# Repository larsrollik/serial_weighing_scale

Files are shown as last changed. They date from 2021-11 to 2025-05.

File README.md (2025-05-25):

# Serial Weighing Scale
Arduino-based cheap precision weighing scale for readout via serial communication.

***
Version: "2.0.4"

Precision weighing scales that include serial port communication usually come at considerable cost. This project showcases an affordable alternative.
Using readily available electronics parts, the scale's measurements can be read via serial communication by a simple Python class.

_Note:_ The design could easily be extended with an Arduino display to show the measurements.

### Bill of Materials
- Arduino Uno (including USB-A to USB-B cable)
- Load cell amplifier HX711 (Sparkfun), e.g. from mouser.co.uk: 474-SEN-13879
- Load cell (100g and 500g cells used), e.g. from mouser.co.uk: 474-SEN-14727 or 474-SEN-14728
- Jumper wires, pin headers, nylon spacers for electronics
- Acrylic or other material of choice for case and load cell mount
- HX711 arduino library from [olkal/HX711_ADC](https://github.com/olkal/HX711_ADC)

### Build
1. Load .ino onto Arduino (via Arduino IDE or commandline like `arduino --board arduino:avr:uno --port /dev/ttyACM0 --upload serial_scale.ino`)
2. Assemble electronics, e.g. as described in this [HX711 wiring tutorial]
3. Print 3D components from [drawings](./drawings_for_3D_printing) (Drawings named `model` are only for design, no need to print these)
4. Move electronics into case
5. Calibrate scale via Arduino IDE serial monitor commands. See below for communication protocol for calibration.

### Usage
1. Connect scale via USB to machine that is going to read the measurements from the scale
2. Interact via python `SerialScale` object:

##### Open connection with `SerialWeighingScale` object & perform standard operations on it
```python
import numpy as np
import time

from serial_weighing_scale import SerialWeighingScale

serial_port = "/dev/ttyACM0"  # for Unix systems. "COM1" on Windows systems
scale = SerialWeighingScale(serial_port=serial_port)
scale.connect()

while not scale.is_ready:
    time.sleep(.1)

# Perform standard operations
scale.tare()  # Tare scale
scale.read_weight()  # Take single measurement
scale.read_weight_repeated(n_readings=5, inter_read_delay=.1)  # Get n readings
scale.read_weight_reliable(n_readings=5, inter_read_delay=.1, measure=np.mean)  # Get statistic of n readings

```

##### Open connection by testing specific serial ports sequentially
```python
from serial_weighing_scale import connect_serial_scale

scale = connect_serial_scale(serial_port_list=["/dev/ttyACM0", "/dev/ttyACM1"])

# ...

```

### Communication protocol for messages between python and Arduino

- Tare scale: send "t" -> Tare scale & Arduino confirms with "t"
- Read scale: send "w" -> Arduino returns latest reading
- Read calibration factor: send "f" -> Arduino returns calibration factor

- Calibrate scale: send "c" + weight of known mass
  - Arduino confirms by sending known mass value back
  - Send "a" once known mass was placed on scale -> Arduino performs calibration & returns new calibration factor that needs to be added to `serial_scale.ino`

### TODO
- [ ] Add calibration routine to .ino & .py
- [ ] Add test curve to .py

## NOTES
- calibration for first scale with 28.22g weight: -3150
- calibration for second scale with 28.22g weight: -2894

### Contributors
Code & electronics by Lars Rollik.
Scale 3D printing drawings by Simon Townsend ([Advanced Manufacturing FabLabs], Sainsbury Wellcome Centre).
Thanks to Benjamin Hahl for useful input on the design.

[Advanced Manufacturing FabLabs]: https://www.sainsburywellcome.org/web/content/fablab
[HX711 wiring tutorial]: https://learn.sparkfun.com/tutorials/load-cell-amplifier-hx711-breakout-hookup-guide

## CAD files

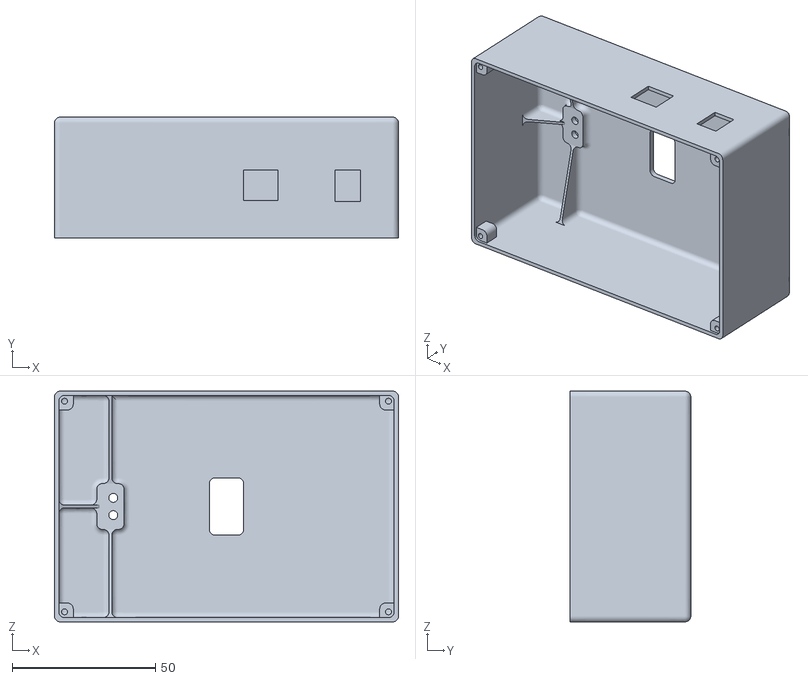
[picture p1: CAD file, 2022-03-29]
drawings_for_3D_printing/serial_weighing_scale__case_main.stl
120.0 x 42.1 x 80.5

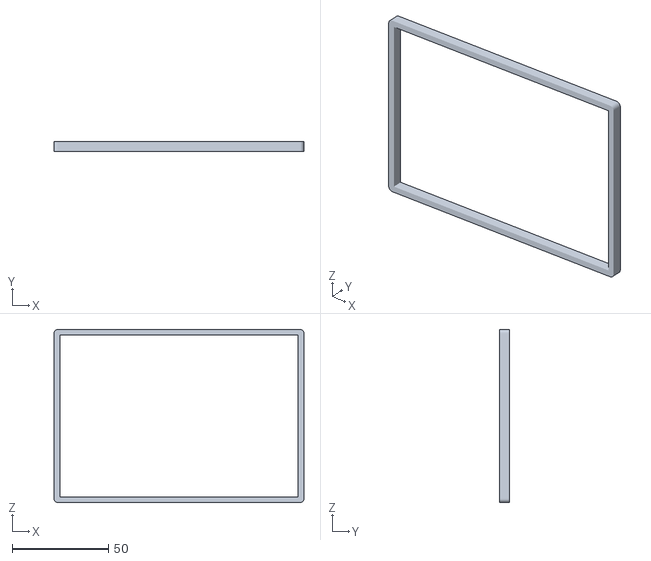
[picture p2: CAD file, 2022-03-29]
drawings_for_3D_printing/serial_weighing_scale__platform_edge_overhang.stl
130.0 x 5.00 x 90.0

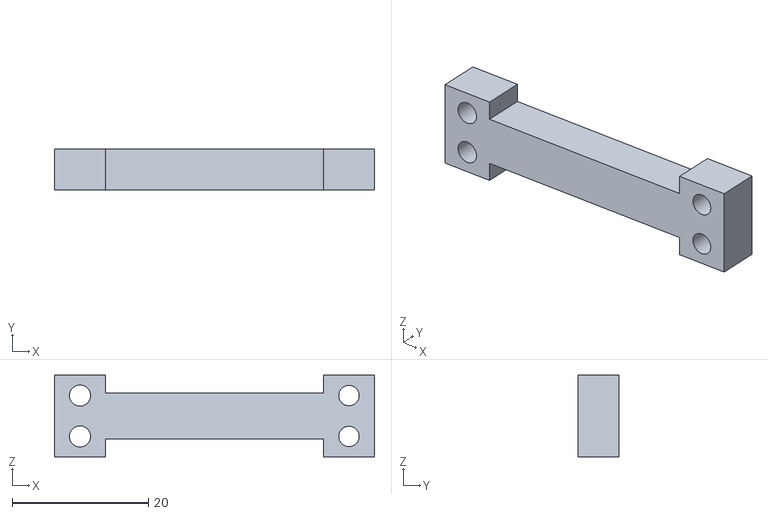
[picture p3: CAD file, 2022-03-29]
drawings_for_3D_printing/serial_weighing_scale__model_load_cell.stl
47.0 x 6.00 x 12.0

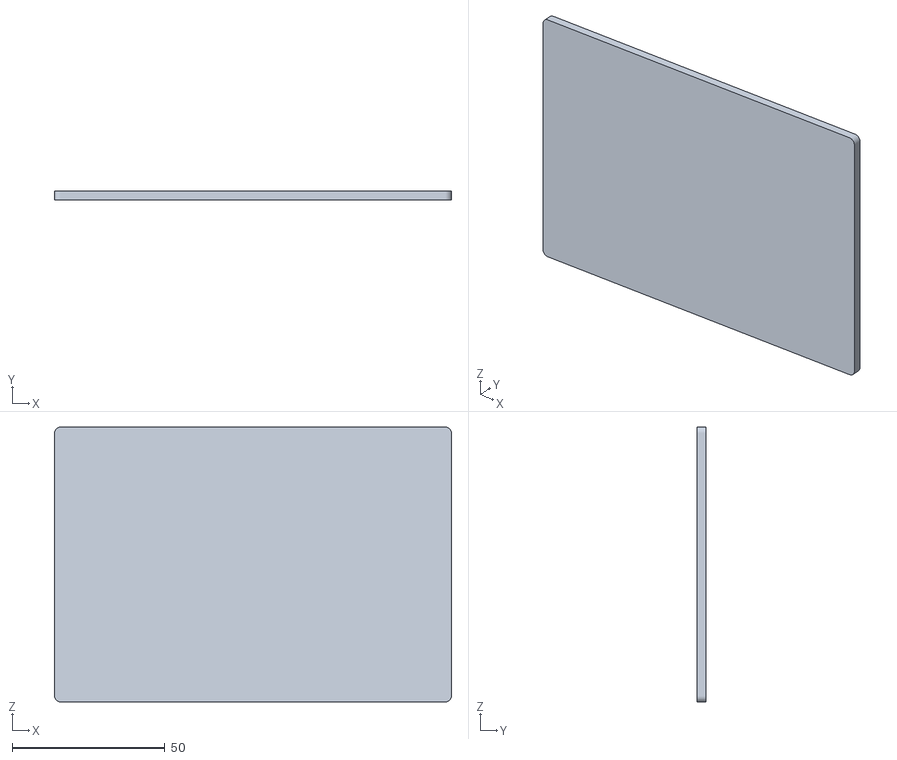
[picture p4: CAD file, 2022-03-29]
drawings_for_3D_printing/serial_weighing_scale__platform.stl
130.0 x 3.00 x 90.0

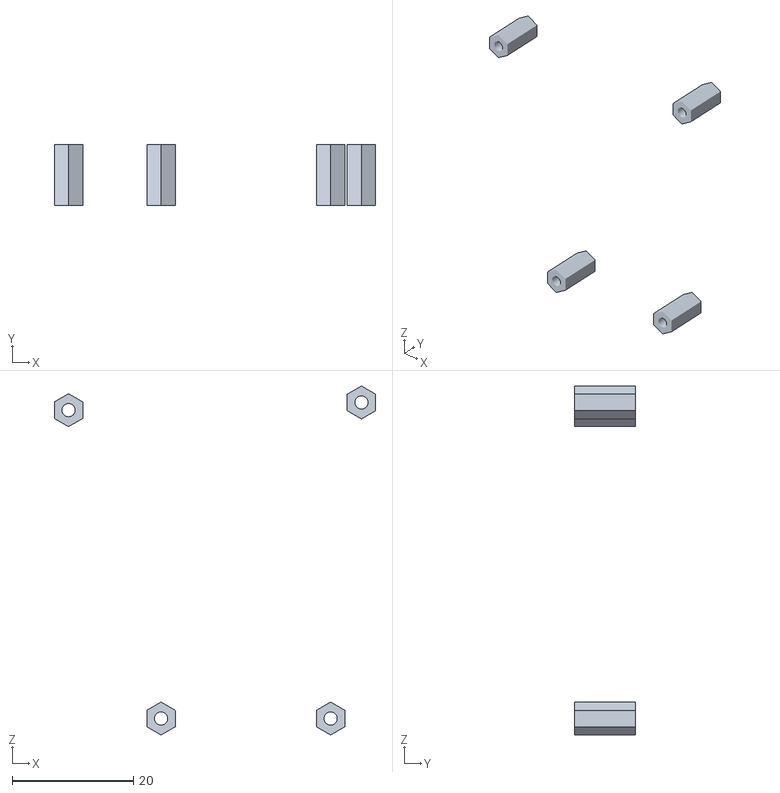
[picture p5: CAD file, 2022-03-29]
drawings_for_3D_printing/serial_weighing_scale__model_standoffs.stl
53.0 x 10.00 x 57.5

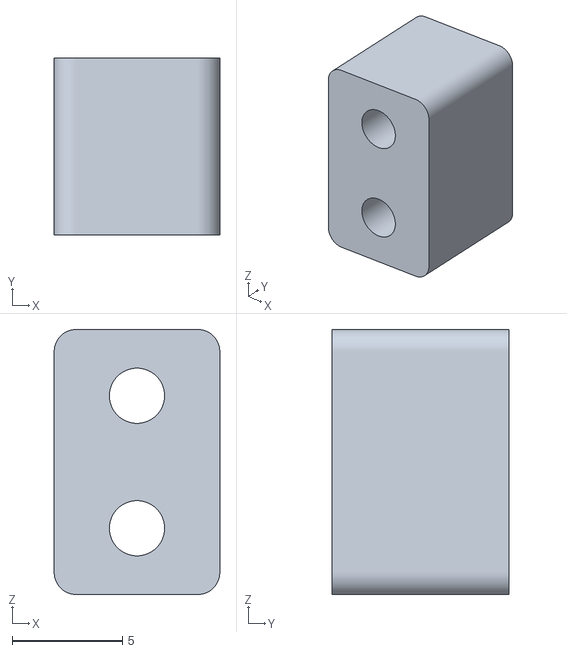
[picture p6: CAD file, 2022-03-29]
drawings_for_3D_printing/serial_weighing_scale__platform_spacer.stl
7.50 x 8.00 x 12.0

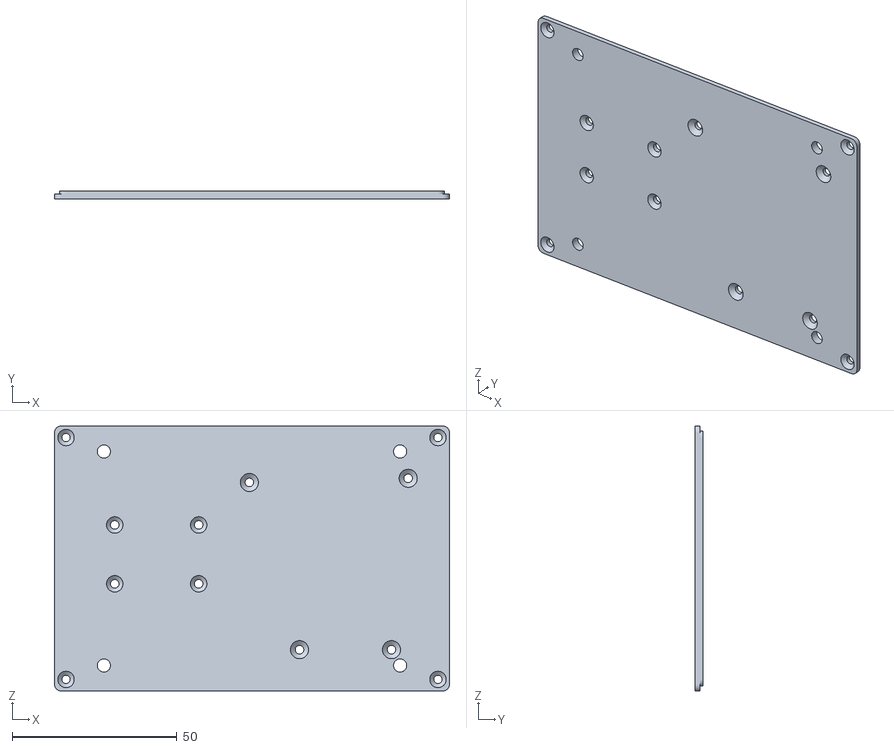
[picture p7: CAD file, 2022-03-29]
drawings_for_3D_printing/serial_weighing_scale__case_base.stl
120.0 x 2.50 x 80.5

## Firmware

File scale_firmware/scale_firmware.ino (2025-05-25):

/*
  Firmware version: "2.0.4"
  -------------------------------------------------------------------------------------
  Adapted example from HX711 library for `serial-weighing-scale`. Lars Rollik, nov2021.
  github.com/larsrollik/serial-weighing-scale
  -------------------------------------------------------------------------------------
  HX711_ADC
  Arduino library for HX711 24-Bit Analog-to-Digital Converter for Weight Scales
  Olav Kallhovd sept2017
  -------------------------------------------------------------------------------------
*/

#include <HX711_ADC.h>

// DEFINITIONS
#define CMD Serial
#define HX711_DOUT 2      // DATA
#define HX711_SCK 3       // CLOCK
#define SAMPLES_IN_USE 1  // number of samples to average for measurement, less will cause more noise but faster response
// #define CALIBRATION_FACTOR -3150  // CHANGE THIS VALUE FROM CALIBRATION RESULT  // scale 1
#define CALIBRATION_FACTOR -2630  // CHANGE THIS VALUE FROM CALIBRATION RESULT  // scale 2
#define SCALING_FACTOR 1.0
#define STABILIZING_TIME 2000  // precision right after power-up can be improved by adding a few seconds of stabilizing time
#define PERFORM_TARE true      // set to false if you don't want tare to be performed in the next step
#define DEBUG_PRINT false
#define ID_STRING "<SerialWeighingScale>"
#define BUFFER_SIZE 10

// INSTANCE of LoadCell object
HX711_ADC LoadCell(HX711_DOUT, HX711_SCK);

float buffer[BUFFER_SIZE];
uint8_t bufIndex = 0;
bool bufFilled = false;
// Sampling flag set by ISR
volatile bool sampleFlag = false;

void setup() {
  // establish communication
  CMD.begin(115200);

  // initialize the scale
  LoadCell.begin();
  LoadCell.start(STABILIZING_TIME, PERFORM_TARE);
  LoadCell.setSamplesInUse(SAMPLES_IN_USE);
  LoadCell.setGain(128);

  if (LoadCell.getTareTimeoutFlag()) {
    logMessage("Timeout, check MCU>HX711 wiring and pin designations");
    while (1)
      ;
  } else {
    LoadCell.setCalFactor(CALIBRATION_FACTOR);
  }

  while (!CMD)
    ;

  identifyMyself();

  if (DEBUG_PRINT)
    logMessage("ready");

  // Initialize buffer
  for (int i = 0; i < BUFFER_SIZE; i++) {
    buffer[i] = 0;
  }

  // --- Timer1 Setup for 100ms interrupts ---
  noInterrupts();  // Disable interrupts during setup

  TCCR1A = 0;  // Clear Timer/Counter Control Registers
  TCCR1B = 0;
  TCNT1 = 0;  // Clear timer counter

  // Set compare match register for 100ms interval
  // Formula: OCR1A = (16*10^6) / (prescaler * frequency) - 1
  // For 10Hz (100ms): OCR1A = 16,000,000 / (64 * 10) - 1 = 24,999
  OCR1A = 24999;
  TCCR1B |= (1 << WGM12);               // CTC mode
  TCCR1B |= (1 << CS11) | (1 << CS10);  // Prescaler 64
  TIMSK1 |= (1 << OCIE1A);              // Enable Timer1 compare interrupt

  interrupts();  // Enable global interrupts

}  // setup


void loop() {
  if (sampleFlag) {
    sampleFlag = false;

    if (LoadCell.update()) {
      addToBuffer(LoadCell.getData());
    }
  }//if

  //   LoadCell.refreshDataSet();
  // LoadCell.update();
  //   float i = LoadCell.getData() / SCALING_FACTOR;

  static byte startByte = '<';
  static byte stopByte = '>';
  static byte commandChar;
  // static uint16_t int1;
  // static uint16_t int2;

  static bool receiving = false;
  static byte buffer[256];
  static int bufferIndex = 0;

  // Check if data is available
  while (CMD.available()) {
    byte incomingByte = CMD.read();

    if (incomingByte == startByte) {
      // Start receiving message
      receiving = true;
      bufferIndex = 0;
      continue;
    }

    // EVAL: Stop receiving message and process data
    if (incomingByte == stopByte) {
      receiving = false;
      commandChar = buffer[0];

      switch (commandChar) {
        case 'i':
          // identify as scale
          identifyMyself();
          break;

        case 'w':
          // read weight

          if (DEBUG_PRINT)
            logMessage("reading weight");

          // readWeight();
          CMD.println(String(getRollingAverage(2)));
          break;

        case 't':
          // tare scale
          tare_scale();
          break;

        case 'c':
          // calibrate scale (factor)
          calibrate();
          break;

        case 'f':
          // read calibration factor
          CMD.println(String(CALIBRATION_FACTOR));
          break;

        default:
          if (DEBUG_PRINT)
            logMessage("Invalid command");
          break;
      }
    }  // EVAL

    // RX
    if (receiving) {
      // Store received bytes in buffer
      if (bufferIndex < sizeof(buffer)) {
        buffer[bufferIndex++] = incomingByte;
      }
    }  // RX
  }    // while
}  // loop


// Timer interrupt handler for sampling
void sampleLoadCell() {
  if (LoadCell.update()) {
    float sample = LoadCell.getData();  // Read sample from HX711
    addToBuffer(sample);
  }
}

// Timer1 ISR every 100ms
ISR(TIMER1_COMPA_vect) {
  sampleFlag = true;
}

// Add the new sample to the buffer
void addToBuffer(float val) {
  buffer[bufIndex++] = val;
  if (bufIndex >= BUFFER_SIZE) {
    bufIndex = 0;
    bufFilled = true;
  }
}

float getRollingAverage(int precision) {
  uint8_t size = bufFilled ? BUFFER_SIZE : bufIndex;
  if (size == 0) return 0.0;

  float sum = 0;
  for (uint8_t i = 0; i < size; i++) sum += buffer[i];
  float avg = sum / size;

  // Round to specified precision
  float factor = pow(10, precision);
  return round(avg * factor) / factor;
}


void identifyMyself() {
  CMD.println(ID_STRING);
}

void logMessage(const String& msg) {
  CMD.print("LOG: ");
  CMD.println(msg);
}  // end:log


void sendFloatAsBytes(float value) {
  union {
    float f;
    byte b[4];
  } data;

  data.f = value;

  for (int i = 0; i < 4; i++) {
    CMD.write(data.b[i]);
  }
}  // end:float

void readWeight() {
  if (DEBUG_PRINT)
    logMessage("fct: readWeight");

  // LoadCell.refreshDataSet();
  LoadCell.update();
  float i = LoadCell.getData() / SCALING_FACTOR;
  // sendFloatAsBytes(i);
  CMD.println(String(i));
}  // end: read weight

int tare_scale() {
  // LoadCell.tareNoDelay();  // Start tare without delay
  LoadCell.tare();  // Start tare (blocking)
}  // end: tare


void calibrate() {
  LoadCell.setCalFactor(1.0);  // Reset calibration factor to default
  tare_scale();                // Tare the scale before calibration

  logMessage("Make sure to send 'c' calibrate command and known mass float each without line ending!");
  logMessage("Please enter the known mass (in grams) and press Enter:");
  while (!CMD.available()) {
    // Wait for the user to submit the known mass
    delay(100);
  }

  // Read the known mass input from serial
  float known_mass = CMD.parseFloat();
  logMessage("Known mass received: ");
  logMessage(String(known_mass));  // Confirm receipt of known mass

  logMessage("Now, please place the known weight on the scale and press 'a' to begin calibration.");

  boolean weight_added = false;
  while (!weight_added) {
    if (CMD.available()) {
      char cmdChar = CMD.read();  // Read input from user
      LoadCell.update();          // Update load cell reading

      // Wait for user to confirm the weight is placed and press 'a'
      if (cmdChar == 'a') {
        LoadCell.refreshDataSet();  // Refresh data from the load cell
        float new_calibration_factor = LoadCell.getNewCalibration(known_mass);

        logMessage("New calibration factor: ");
        logMessage(String(new_calibration_factor));

        weight_added = true;  // Calibration is complete
      }
    }
    delay(10);  // Short delay to avoid excessive CPU usage
  }             // while
}  // end: calibrate

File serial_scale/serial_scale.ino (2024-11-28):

/*
   Adapted example from HX711 library for `serial_weighing_scale`. Lars Rollik, nov2021.
   github.com/larsrollik/serial_weighing_scale
   -------------------------------------------------------------------------------------
   HX711_ADC
   Arduino library for HX711 24-Bit Analog-to-Digital Converter for Weight Scales
   Olav Kallhovd sept2017
   -------------------------------------------------------------------------------------
*/

#include <HX711_ADC.h>

// DEFINITIONS
#define CMD Serial
#define HX711_DOUT 2              // DATA
#define HX711_SCK 3               // CLOCK
#define SAMPLES_IN_USE 1          // number of samples to average for measurement, less will cause more noise but faster response
#define CALIBRATION_FACTOR -3150  // CHANGE THIS VALUE FROM CALIBRATION RESULT
#define SCALING_FACTOR 1.0
#define STABILIZING_TIME 2000  // precision right after power-up can be improved by adding a few seconds of stabilizing time
#define PERFORM_TARE true      // set to false if you don't want tare to be performed in the next step
#define DEBUG_PRINT false


// INSTANCE of LoadCell object
HX711_ADC LoadCell(HX711_DOUT, HX711_SCK);


void setup() {
  LoadCell.begin();
  LoadCell.start(STABILIZING_TIME, PERFORM_TARE);
  LoadCell.setSamplesInUse(SAMPLES_IN_USE);

  CMD.begin(115200);
  while (!CMD)
    ;

  if (LoadCell.getTareTimeoutFlag()) {
    CMD.println("Timeout, check MCU>HX711 wiring and pin designations");
    while (1)
      ;
  } else {
    LoadCell.setCalFactor(CALIBRATION_FACTOR);

    if (DEBUG_PRINT)
      CMD.println("READY");
  }
}

void loop() {
  //   LoadCell.refreshDataSet();
  //   LoadCell.update();
  //   float i = LoadCell.getData() / SCALING_FACTOR;

  if (CMD.available()) {
    char cmdChar = CMD.read();

    if (DEBUG_PRINT) {
      CMD.println("cmd: " + String(cmdChar));  // Print cmdChar for debugging
    }

    if (cmdChar == 'w') {
      unsigned long startTime = millis();

      LoadCell.refreshDataSet();
      LoadCell.update();
      float i = LoadCell.getData() / SCALING_FACTOR;
      CMD.println(i);

      if (DEBUG_PRINT) {
        unsigned long endTime = millis();  // Record the end time
        // Calculate and print the elapsed time
        unsigned long dt = endTime - startTime;
        CMD.println("Time taken (dt): " + String(dt) + " ms");
      }  //if
    }    //if

    if (cmdChar == 't') {

      if (DEBUG_PRINT) {
        CMD.println("taring");  // Print cmdChar for debugging
      }

      tare_scale();

      CMD.println("t");

    }  //if

    if (cmdChar == 'c') {

      calibrate();
    }  //if

    if (cmdChar == 'r') {

      CMD.println("{'calibration_factor': " + String(CALIBRATION_FACTOR) + "}");
    }  //if

  }  //cmd serial input
}  //loop

// Function to tare the scale
int tare_scale() {
  // LoadCell.tareNoDelay();  // Start tare without delay
  LoadCell.tare();  // Start tare (blocking)

  // unsigned long startTime = millis();  // Track the time to avoid infinite waiting

  // // Wait for the tare process to finish, with a timeout
  // if (LoadCell.getTareStatus() == true) {
  //   Serial.println("Tare complete");
  // }
  // while (LoadCell.getTareStatus() != true) {
  //   // Check if the process has taken too long
  //   if (millis() - startTime > 5000) {  // 5-second timeout, adjust as needed
  //     return 1;  // Tare failed due to timeout
  //   }
  //   delay(10);  // Small delay to avoid busy-waiting too aggressively
  // }

  // // If the tare is complete, send confirmation byte and return 0 (success)
  // CMD.write(0);  // Send confirmation byte (0) after tare completion
  // return 0;  // Tare succeeded
}


void calibrate() {
  LoadCell.setCalFactor(1.0);  // Reset calibration factor to default
  tare_scale();                // Tare the scale before calibration

  CMD.println("Make sure to send 'c' calibrate command and known mass float each without line ending!");
  CMD.println("Please enter the known mass (in grams) and press Enter:");
  while (!CMD.available()) {
    // Wait for the user to submit the known mass
    delay(100);
  }

  // Read the known mass input from serial
  float known_mass = CMD.parseFloat();
  CMD.print("Known mass received: ");
  CMD.println(known_mass);  // Confirm receipt of known mass

  CMD.println("Now, please place the known weight on the scale and press 'a' to begin calibration.");

  boolean weight_added = false;
  while (!weight_added) {
    if (CMD.available()) {
      char cmdChar = CMD.read();  // Read input from user
      LoadCell.update();          // Update load cell reading

      // Wait for user to confirm the weight is placed and press 'a'
      if (cmdChar == 'a') {
        LoadCell.refreshDataSet();  // Refresh data from the load cell
        float new_calibration_factor = LoadCell.getNewCalibration(known_mass);

        CMD.print("New calibration factor: ");
        CMD.println(new_calibration_factor);

        weight_added = true;  // Calibration is complete
      }
    }
    delay(10);  // Short delay to avoid excessive CPU usage
  }
}

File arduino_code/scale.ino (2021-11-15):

/*
   Adapted example from HX711 library for SerialWeightScale. Lars Rollik, nov2021.
   -------------------------------------------------------------------------------------
   HX711_ADC
   Arduino library for HX711 24-Bit Analog-to-Digital Converter for Weight Scales
   Olav Kallhovd sept2017
   -------------------------------------------------------------------------------------
*/

#include <HX711_ADC.h>

const int HX711_dout = 2; // DATA
const int HX711_sck  = 3; // CLOCK

HX711_ADC LoadCell(HX711_dout, HX711_sck);

const float calibrationValue = -591.67; // calibration value (see example file "Calibration.ino")
const float scalingFactor = 5.28;

unsigned long stabilizingtime = 2000; // preciscion right after power-up can be improved by adding a few seconds of stabilizing time
boolean _tare = true; //set this to false if you don't want tare to be performed in the next step

void setup() {
  Serial.begin(57600); delay(10);

  LoadCell.begin();
  LoadCell.start(stabilizingtime, _tare);

  if (LoadCell.getTareTimeoutFlag()) {
    Serial.println("Timeout, check MCU>HX711 wiring and pin designations");
    while (1);
  }
  else {
    LoadCell.setCalFactor(calibrationValue);
  }
}

void loop() {
  LoadCell.update();
  float i = LoadCell.getData() / scalingFactor;

  if (Serial.available() > 0) {
    char inByte = Serial.read();

    // Tare
    if (inByte == 't') {
      LoadCell.tareNoDelay();

      if (LoadCell.getTareStatus() == true) {
        //  Serial.println("Tare complete");
      }
    }

    // Calibrate
    if (inByte == 'c') {
      calibrate();
    }

    // Read weight
    if (inByte == 'w') {
      Serial.println(i);
    }

  } // serial
} // loop


void calibrate() {
  /*
     TODO
  */
}

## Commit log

2022-03-15 updated with templatepy contents. refactored into installable package + arduino code dir
2022-03-27 moved arduino code to correct arduino project nesting. extended ino by calibration routine that is mirrored in serial object py class
2022-03-27 update of scale functions and outlined logic for calibration. works from Arduino IDE serial monitor but returns wrong calibration values in python (typecasting?)
2022-03-27 "Upgrade: 0.0.0.dev1 → 0.0.0.rc0"
2022-03-27 "Upgrade: 0.0.0.rc0 → 0.0.1.dev0"
2022-03-27 "Upgrade: 0.0.1.dev0 → 0.0.1"
2022-03-27 "Upgrade: 0.0.1 → 0.0.2.dev0"
2022-03-27 "Upgrade: 0.0.2.dev0 → 0.0.2"
2022-03-28 "Upgrade: 0.0.2 → 0.0.3.dev0"
2022-03-28 "Upgrade: 0.0.3.dev0 → 0.0.3"
2022-03-28 "Upgrade: 0.0.3 → 0.0.4.dev0"
2022-03-29 drawings for 3D printing
    [serial_weighing_scale__case_base.stl, serial_weighing_scale__case_main.stl, serial_weighing_scale__model_load_cell.stl, serial_weighing_scale__model_standoffs.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]
2022-03-29 "Upgrade: 0.0.4.dev0 → 0.0.4"
2022-03-29 "Upgrade: 0.0.4 → 0.0.5.dev0"
2022-03-29 "Upgrade: 0.0.5.dev0 → 0.0.5"
2022-03-29 "Upgrade: 0.0.5 → 0.0.6.dev0"
2022-03-29 "Upgrade: 0.0.6.dev0 → 0.0.6"
2024-11-16 work on updated protocol for weighing scale
    [serial_weighing_scale__case_base.stl, serial_weighing_scale__case_main.stl, serial_weighing_scale__model_load_cell.stl, serial_weighing_scale__model_standoffs.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]
2024-11-16 updated arduino firmware and re-calibrated
2024-11-20 "Upgrade: 0.0.6 → 1.0.0.dev0"
2024-11-20 "Upgrade: 1.0.0.dev0 → 1.0.0"
2024-11-28 note on calibration factors and readout of factor from device
2025-03-20 print -> log debug
2025-03-20 "Upgrade: 1.0.0 → 1.0.1.dev0"
2025-03-20 "Upgrade: 1.0.1.dev0 → 1.0.1"
2025-05-07 Major refactor of serial scale code including the underlying Arduino firmware and API protocol.
2025-05-07 "Upgrade: 1.0.1 → 2.0.0.dev0"
2025-05-07 "Upgrade: 2.0.0.dev0 → 2.0.0"
2025-05-07 fixed connecting issue, when multiple serial devices present. added logic to identify scale.
2025-05-07 "Upgrade: 2.0.0 → 2.0.1.dev0"
2025-05-07 "Upgrade: 2.0.1.dev0 → 2.0.1"
2025-05-08 "Upgrade: 2.0.1 → 2.0.2.dev0"
2025-05-08 "Upgrade: 2.0.2.dev0 → 2.0.2"
2025-05-08 arduino firmware upgraded with circular buffer and interrupt sampling
2025-05-08 "Upgrade: 2.0.2 → 2.0.3.dev0"
2025-05-08 "Upgrade: 2.0.3.dev0 → 2.0.3"
2025-05-25 "Upgrade: 2.0.3 → 2.0.4.dev0"
2025-05-25 "Upgrade: 2.0.4.dev0 → 2.0.4"
